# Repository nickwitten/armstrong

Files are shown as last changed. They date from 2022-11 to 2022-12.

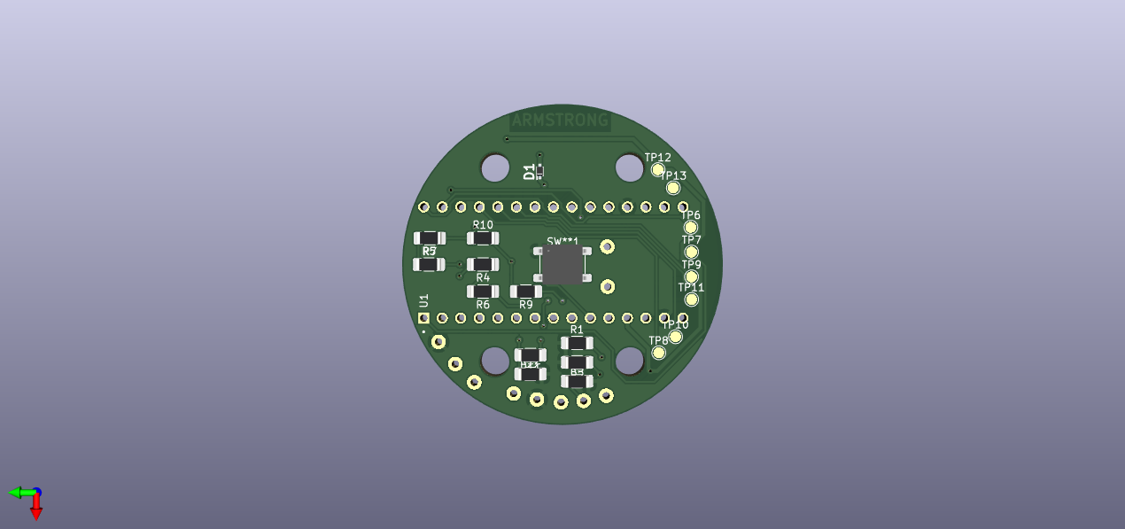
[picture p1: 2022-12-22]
poster_figures/Armstrong_v2.0_PCB_3D_Back.png

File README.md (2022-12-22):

# ARMSTRONG

Armstrong is a functional electrical stimulation (FES) project aimed to help individuals with spinal chord injuries. The loss of dexterity in the fingers and hand makes day-to-day life much more difficult. The wearable watch has two electrodes that are placed on the user's arm to stimulate the forearm muscles which elicits a grasping motion.

The project contains two PCB designs located in
/ArmstrongPCB/
for a transformer based stimulation circuit and also a boost/H-bridge based stimulation circuit for more waveform options and amplitude.

The project also contains the firmware located in
/ArmstrongSoftware/
which can be flashed to an Arduino. There is separate firmware for the transformer based circuit and the boost/H-bridge based circuit.

The directory
/deliverables/
contains all of the design files that were used in the final product. A lot of other folders were used for exploring ideas and debugging.

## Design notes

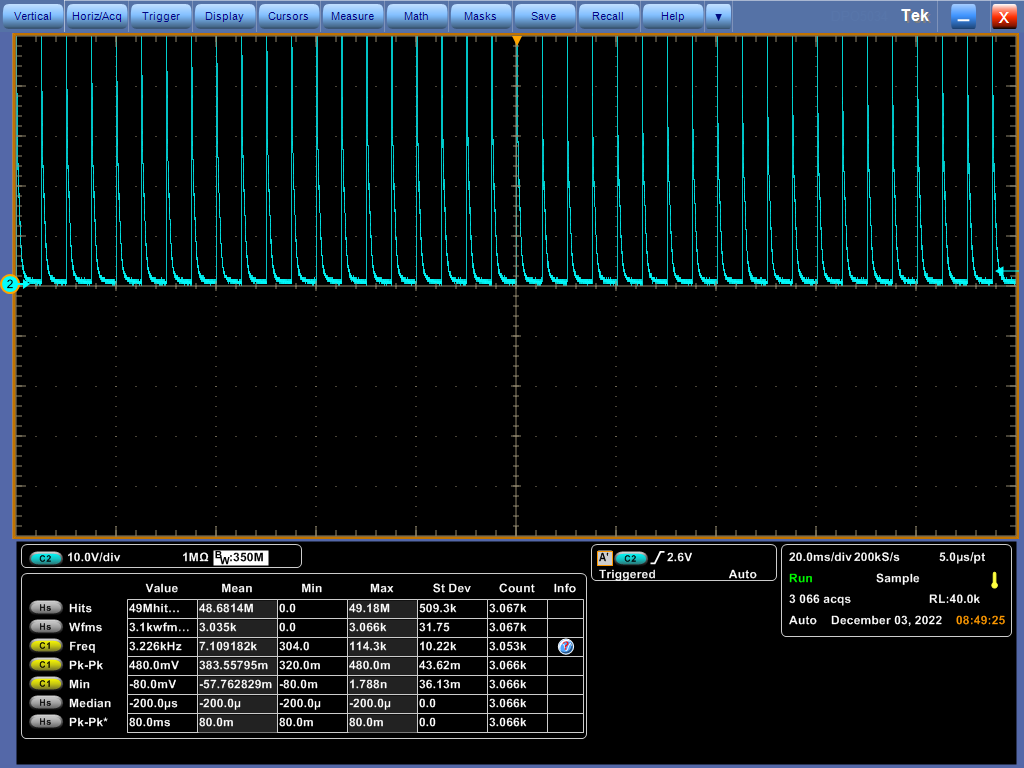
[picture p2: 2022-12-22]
poster_figures/wave_pulse.png

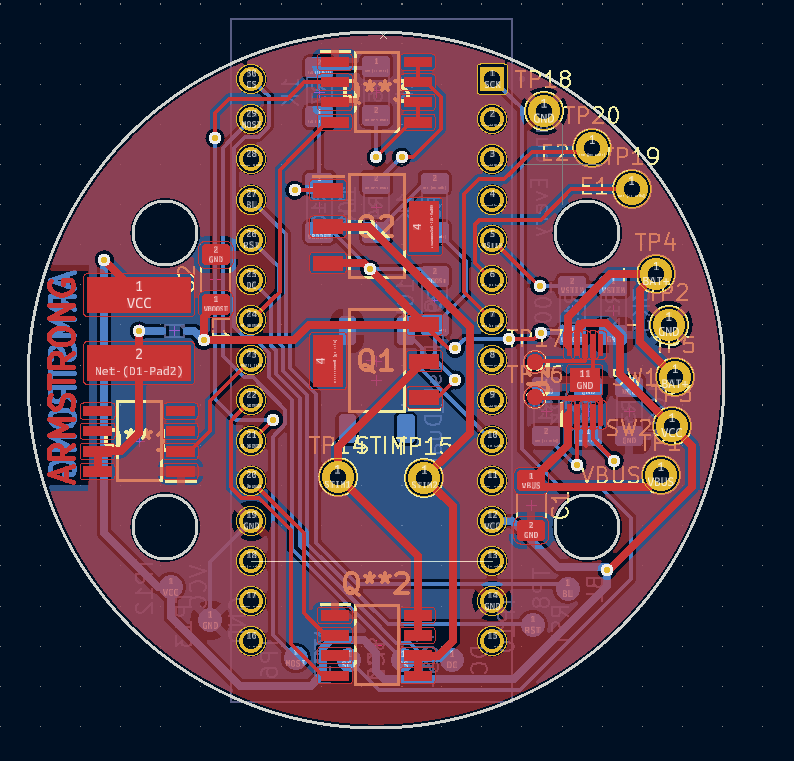
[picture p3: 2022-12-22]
poster_figures/Armstrong_v2.0_PCB_Layout..png

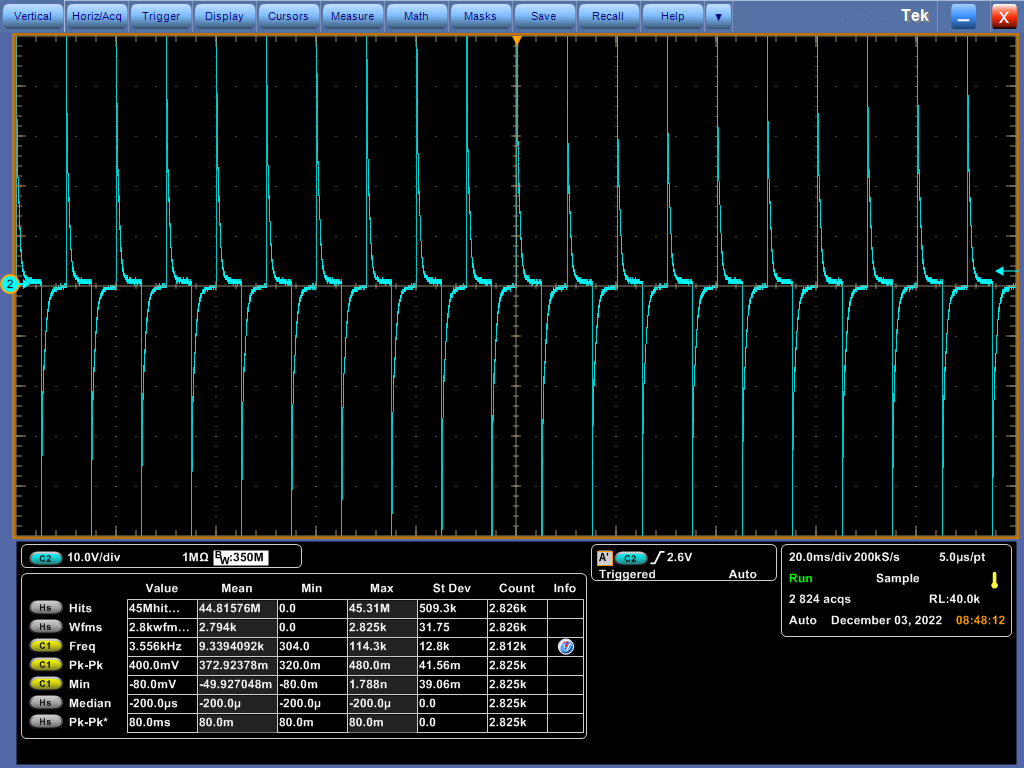
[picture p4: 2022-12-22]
poster_figures/wave_differential_high_amp.png

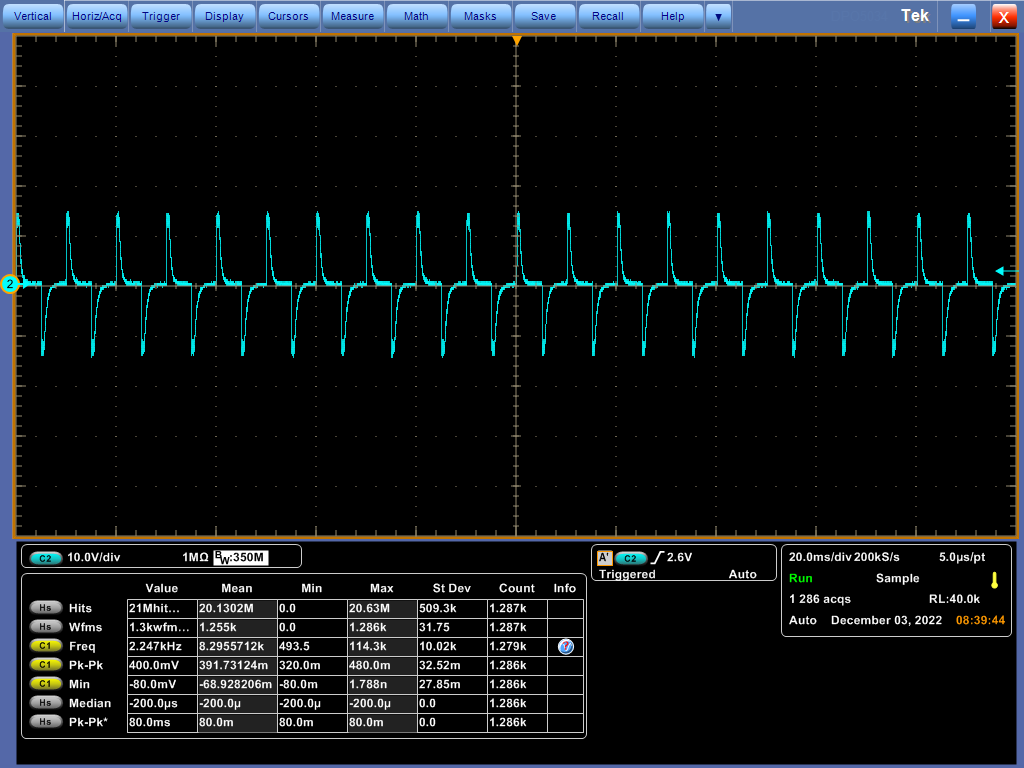
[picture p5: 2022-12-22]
poster_figures/wave_differential_low_amp.png

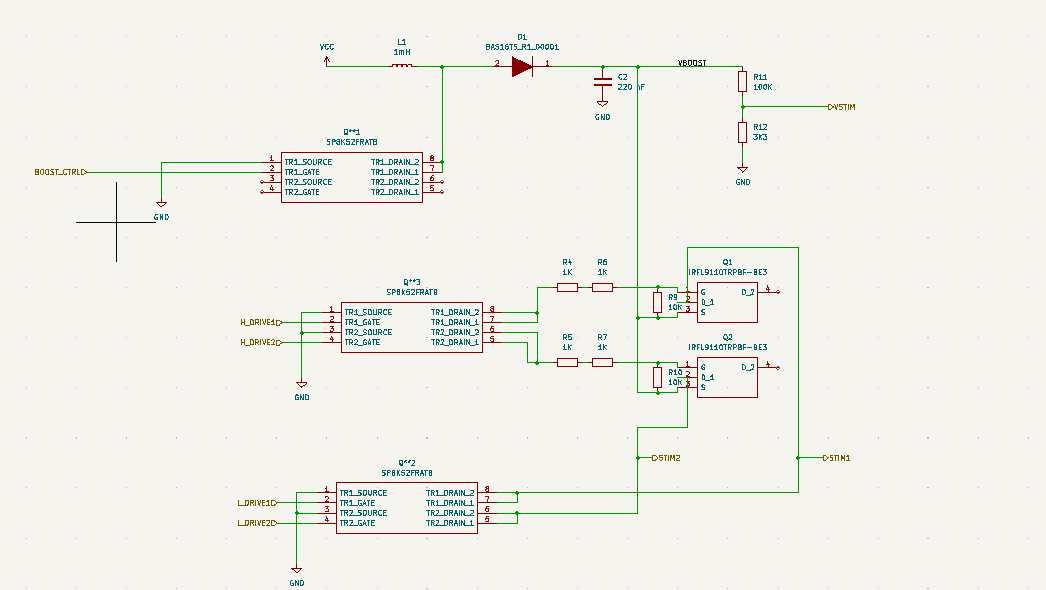
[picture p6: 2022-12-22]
poster_figures/Armstrong_v2.0_Schematic_Stim.png

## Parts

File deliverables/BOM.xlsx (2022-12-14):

 | Item | Supplier | Part# | Manufacturer# | Description | Qty | Price
Primary | 1A | Amazon | GC9A01 | Waveshare | 1.28 Inch Round LCD | 2 | $41.38
Direct Link: | https://www.amazon.com/1-28inch-Display-Resolution-Interface-Raspberry/dp/B08VGT2T42/
Alternative | 1B | Waveshare | GC9A01 | Waveshare | 1.28 Inch Round LCD | 2 | $41.38
Direct Link: | https://www.waveshare.com/product/1.28inch-lcd-module.htm
Primary | 2A | Amazon | B072CFZX8W | JAYSSS | 0.2mm Copper Sheet | 2 | $27.80
Direct Link: | https://www.amazon.com/0-2mm-Thickness-Copper-Purity-100mmx1000mm/dp/B07ZCFZX8W/
Alternative | 2B | Amazon | B098YZ16Y9 | Craft Wire | 32 Guage Copper Sheet | 2 | $37.98
Direct Link: | https://www.amazon.com/99-9-Copper-Sheet-Gauge-Blank/dp/B098YZ16Y9?th=1
Primary | 3A | Digikey | 2449-CS1204AF260CT-ND - Cut Tape (CT) | CIT Relay and Switch | SMD Tactile Button | 10 | $3.81
Direct Link: | https://www.digikey.com/en/products/detail/cit-relay-and-switch/CS1204AF260/12502958
Alternative | 3B | If Can't Buy Let Us Know
Direct Link:
 | Item | Supplier | Part# | Manufacturer# | Description | Qty | Price
Primary | 4A | Amazon | a19101700ux0341 | uxcell | uxcell 6710-2RS Deep Groove Ball Bearings 50mm x 62mm x 6mm Double Sealed Chrome Steel Z2 ABEC1 | 2 | $19.98
Direct Link: | https://www.amazon.com/uxcell-6710-2RS-Groove-Bearings-Double/dp/B085NDHJ8F?th=1
Alternative | 4B | AliExpress | 6710ZZ | Sunshine Xixi | 1pcs ultra-thin deep groove ball bearings 6710ZZ 50*62*6 mm | 2 | $13.86
Direct Link: | https://www.aliexpress.us/item/2251832472419159.html
Primary | 5A | Digikey | MT4148-ND | MET-23 | TRANSFORMER 1.6KCT:3.2 2.5MADC | 2 | $23.20
Direct Link: | https://www.digikey.com/en/products/detail/tamura/MET-23/285665
Alternative | 5B
Direct Link:
 | Item | Supplier | Part# | Manufacturer# | Description | Qty | Price
Primary | 6A | Texas Instruments | LM2937ES-3.3-ND | LM2937ES-3.3 | IC REG LIN 3.3V 500MA DDPAK | 5 | $16.70
Direct Link: | https://www.digikey.com/en/products/detail/texas-instruments/LM2937ES-3-3/3701317
Alternative | 6B
Direct Link:
Primary | 7A |  |  |  | Battery Packs 3.7 V 250mAh 31.5 x 17.0 x 5.7mm
Direct Link: | https://www.mouser.com/ProductDetail/Renata/ICP521630PM?qs=sGAEpiMZZMuXcNZ31nzYhXht66AyoktbAomnvfkiFzU%3D
Alternative | 7B
Direct Link:
 | Item | Supplier | Part# | Manufacturer# | Description | Qty | Price
Primary | 8A | ROHM Semiconductor | 755-SP8K52FRATB | SP8K52FRATB | MOSFET Nch+Nch 100V Vds 3A 0.135Rds(on) 8.5Qg | 5 | $5.55
Direct Link: | https://www.mouser.com/ProductDetail/ROHM-Semiconductor/SP8K52FRATB?qs=sGAEpiMZZMutXGli8Ay4kEWj9pzNwJQ3Ab9nciqoLcQ%3D
Alternative | 8B | ROHM Semiconductor | 755-UM6K31NFHATCN | UM6K31NFHATCN | MOSFET Nch+Nch 60V Vds 3Rds(on) SOT-363 | 5 | $2.60
Direct Link: | https://www.mouser.com/ProductDetail/ROHM-Semiconductor/UM6K31NFHATCN?qs=sGAEpiMZZMutXGli8Ay4kEWj9pzNwJQ3hyJfQAX8x7s%3D
Primary | 9A | Panjit | 241-BAS16TS_R1_00001 | BAS16TS_R1_00001 | Diodes - General Purpose, Power, Switching 100Vll Signal Switching Diodes 4A | 10 | $1.56
Direct Link: | https://www.mouser.com/ProductDetail/Panjit/BAS16TS_R1_00001?qs=sPbYRqrBIVkk0IRTyt6GmQ%3D%3D
Alternative | 9B | onsemi / Fairchild | 512-MMSD4448 | MMSD4448 | Diodes - General Purpose, Power, Switching Hi Conductance Fast | 10 | $2.51
Direct Link: | https://www.mouser.com/ProductDetail/onsemi-Fairchild/MMSD4448?qs=HxNY1oXTrTS1XYzDYVbdxA%3D%3D
Primary | 10A | Analog Devices | 584-ADP122AUJZ-3.3R7 | ADP122AUJZ-3.3-R7 | Linear Voltage Regulators 300mA LDO 3.3Vout | 5 | $8.20
Direct Link: | https://www.mouser.com/ProductDetail/Analog-Devices/ADP122AUJZ-3.3-R7?qs=BpaRKvA4VqERsawSFjb%252Blw%3D%3D
Alternative | 10B | Analog Devices | 584-ADP160AUJZ-3.3R7 | ADP160AUJZ-3.3-R7 | Linear Voltage Regulators 150mA LDO 3.3Vout w/ QOD | 5 | $8.00
Direct Link: | https://www.mouser.com/ProductDetail/Analog-Devices/ADP160AUJZ-3.3-R7?qs=WIvQP4zGanjwQREaBvEWig%3D%3D
Primary | 11A | Analog Devices | 584-ADP162AUJZ-4.2R7 | ADP162AUJZ-4.2-R7 | LDO Voltage Regulators 150mA LDO 4.2Vout | 5 | $8.00
Direct Link: | https://www.mouser.com/ProductDetail/Analog-Devices/ADP162AUJZ-4.2-R7?qs=WIvQP4zGangti17mGJlz9g%3D%3D
Alternative | 11B | Texas Instruments | 595-TPS79942DDCR | TPS79942DDCR | LDO Voltage Regulators Sgl Output LDO 200mA Fixed 4.2V | 5 | $5.20
Direct Link: | https://www.ti.com/lit/ds/symlink/tps799.pdf?HQS=dis-mous-null-mousermode-dsf-pf-null-wwe&ts=1665556814501
 | Item | Supplier | Part# | Manufacturer# | Description | Qty | Price
Primary | 12A | Mouser | 782-ABX00033 | ABX00033 | AVR ARDUINO NANO EVERY | 2 | $33.76
Direct Link: | https://www.mouser.com/ProductDetail/Arduino/ABX00033?qs=PzGy0jfpSMueXyfBfl2XSA%3D%3D
Alternative | 12B | Digikey | 1050-ABX00033-ND | ABX00033 | ARDUINO NANO EVERY WITH HEADERS | 2 | $33.76
Direct Link: | https://www.digikey.com/en/products/detail/arduino/ABX00033/10239972
 | Item | Supplier | Part# | Manufacturer# | Description | Qty | Price
Primary | 13A | Mouser | 755-SP8K52FRATB | SP8K52FRATB | MOSFET Nch+Nch 100V Vds 3A 0.135Rds(on) 8.5Qg | 5 | $5.55
Direct Link: | https://www.mouser.com/ProductDetail/ROHM-Semiconductor/SP8K52FRATB?qs=sGAEpiMZZMutXGli8Ay4kEWj9pzNwJQ3Ab9nciqoLcQ%3D
Alternative | 13B
Direct Link:
Primary | 14A | Mouser | 241-BAS16TS_R1_00001 | BAS16TS_R1_00001 | Diodes - General Purpose, Power, Switching 100Vll Signal Switching Diodes 4A | 10 | $1.56
Direct Link: | https://www.mouser.com/ProductDetail/Panjit/BAS16TS_R1_00001?qs=sPbYRqrBIVkk0IRTyt6GmQ%3D%3D
Alternative | 14B
Direct Link:
Primary | 15A | Mouser | 78-IRFL9110TRPBF-BE3 | IRFL9110TRPBF-BE3 | MOSFET 100V P-CH MOSFET (D-S) | 5 | $10.50
Direct Link: | https://www.mouser.com/ProductDetail/Vishay-Siliconix/IRFL9110TRPBF-BE3?qs=7MVldsJ5UaxpERaG2Aoxtg%3D%3D
Alternative | 15B
Direct Link:
Primary | 16A | Mouser | 595-BQ24093DGQR | BQ24093DGQR | Battery Management 1A,Sgl-Inp,Sgl-Cell Li-Ion Batt Charger | 5 | $8.45
Direct Link: | https://www.mouser.com/ProductDetail/Texas-Instruments/BQ24093DGQR?qs=C44r%252BX3hXgJJomV3RK43zw%3D%3D
Alternative | 16B
Direct Link:
Primary | 17A | Mouser | 994-LPS6225-105MRC | LPS6225-105MRC | Power Inductors - SMD 1 mH Shld 20% 170mA 6Ohms | 5 | $9.10
Direct Link: | https://www.mouser.com/ProductDetail/Coilcraft/LPS6225-105MRC?qs=QQJxVsr8EGZFFDxesxNmXA%3D%3D
Alternative | 17B
Direct Link:
Primary | 18A | Mouser | 80-C1206C105K3NAUTO | C1206C105K3NACAUTO | SMD/SMT 25V 1uF X8L 1206 | 10 | $5.30
Direct Link: | https://www.mouser.com/ProductDetail/KEMET/C1206C105K3NACAUTO
Alternative | 18B | Mouser | 80-C1206F105M5RAUTLR | C1206F105M5RACAUTO7210 | SMD/SMT 50V 1uF X7R 1206 | 10 | $7.30
Direct Link: | https://www.mouser.com/ProductDetail/KEMET/C1206F105M5RACAUTO7210
Primary | 19A | Mouser | 80-C1206C224J1RAUTO | C1206C224J1RACAUTO | SMD/SMT 100V 0.22uF X7R 1206 5% AEC-Q200 | 10 | $8.30
Direct Link: | https://www.mouser.com/ProductDetail/KEMET/C1206C224J1RACAUTO?qs=ds50AKTGxA8%252BykFr3yWSoQ%3D%3D
Alternative | 19B | Mouser | 81-GCJ31MR72A224KA1L | GCJ31MR72A224KA01L | SMD/SMT .22UF 100V 10% 1206 | 10 | $4.80
Direct Link: | https://www.mouser.com/ProductDetail/Murata-Electronics/GCJ31MR72A224KA01L?qs=zThidflJDvanaGTB%252BAWhhA%3D%3D
Primary | 20A | Mouser | 71-RCC12061K00FKEA | RCC12061K00FKEA | SMD 1.0 Kohms 1% 100ppm | 20 | $6.60
Direct Link: | https://www.mouser.com/ProductDetail/Vishay-Dale/RCC12061K00FKEA
Alternative | 20B | Mouser | 755-SFR18EZPF1001 | SFR18EZPF1001 | Thick Film Resistors - SMD | 20 | $9.60
Direct Link: | https://www.mouser.com/ProductDetail/ROHM-Semiconductor/SFR18EZPF1001
Primary | 21A | Mouser | 71-CRMA1206AF10K0DKF | CRMA1206AF10K0DKEF | Thick Film Resistors - SMD 0.30W 10Kohm .5% AEC-Q200 | 10 | $5.90
Direct Link: | https://www.mouser.com/ProductDetail/Vishay/CRMA1206AF10K0DKEF?qs=sGAEpiMZZMtlubZbdhIBIOn2mbhvx7T2u0J1JQj7TEY%3D
Alternative | 21B
Direct Link:
Primary | 22A | Mouser | 71-CRMA1206AF100KFKF | CRMA1206AF100KFKEF | Thick Film Resistors - SMD 0.30W 100Kohm 1% AEC-Q200 | 10 | $5.50
Direct Link: | https://www.mouser.com/ProductDetail/Vishay/CRMA1206AF100KFKEF?qs=QNEnbhJQKvZE9rjcxNiRnA%3D%3D
Alternative | 22B
Direct Link:
Primary | 23A | Mouser | 755-SFR18EZPJ332 | SFR18EZPJ332 | Thick Film Resistors - SMD | 10 | $1.39
Direct Link: | https://www.mouser.com/ProductDetail/ROHM-Semiconductor/SFR18EZPJ332?qs=sGAEpiMZZMtlubZbdhIBIK8AeiPKd8jIg8Se9AlDaOM%3D
Alternative | 23B
Direct Link:
Primary | 24A | Mouser | 755-SFR18EZPF2001 | SFR18EZPF2001 | Thick Film Resistors - SMD | 10 | $2.15
Direct Link: | https://www.mouser.com/ProductDetail/ROHM-Semiconductor/SFR18EZPF2001?qs=sGAEpiMZZMtlubZbdhIBIK8AeiPKd8jIOdUsMKoQsaE%3D
Alternative | 24B
Direct Link:
Primary | 25A | Mouser | 71-TNPW12062K70BEEA | TNPW12062K70BEEA | Thick Film Resistors - SMD | 10 | $7.59
Direct Link: | https://www.mouser.com/ProductDetail/Vishay-Dale/TNPW12062K70BEEA?qs=sGAEpiMZZMtlubZbdhIBIKjNc5kvbugN9Cb1dArGElQ%3D
Alternative | 25B
Direct Link:

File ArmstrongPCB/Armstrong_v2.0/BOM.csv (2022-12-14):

Id | Designator | Package | Quantity | Designation | Supplier and ref
1 | SW**1 | CS1204AF260-SMD | 1 | SW_Push_Dual
2 | TP17 | TestPoint_Pad_D1.0mm | 1 | ~{CHG}
3 | TP16 | TestPoint_Pad_D1.0mm | 1 | PG
4 | C2 | C_1206_3216Metric_Pad1.33x1.80mm_HandSolder | 1 | 220 nF
5 | C1 | C_1206_3216Metric_Pad1.33x1.80mm_HandSolder | 1 | 1uF
6 | D1 | BAS16TS_R1_00001 | 1 | BAS16TS_R1_00001
7 | R12 | R_1206_3216Metric_Pad1.30x1.75mm_HandSolder | 1 | 3K3
8 | R11,R3 | R_1206_3216Metric_Pad1.30x1.75mm_HandSolder | 2 | 100K
9 | R10,R9 | R_1206_3216Metric_Pad1.30x1.75mm_HandSolder | 2 | 10K
10 | R7,R6,R5,R4 | R_1206_3216Metric_Pad1.30x1.75mm_HandSolder | 4 | 1K
11 | R2 | R_1206_3216Metric_Pad1.30x1.75mm_HandSolder | 1 | 2K
12 | R1 | R_1206_3216Metric_Pad1.30x1.75mm_HandSolder | 1 | 2K7
13 | TP13 | TestPoint_Pad_D1.5mm | 1 | GND
14 | TP12 | TestPoint_Pad_D1.5mm | 1 | VCC
15 | TP11 | TestPoint_Pad_D1.5mm | 1 | DC
16 | TP10 | TestPoint_Pad_D1.5mm | 1 | RST
17 | TP9 | TestPoint_Pad_D1.5mm | 1 | CS
18 | TP8 | TestPoint_Pad_D1.5mm | 1 | BL
19 | TP7 | TestPoint_Pad_D1.5mm | 1 | SCK
20 | TP6 | TestPoint_Pad_D1.5mm | 1 | MOSI
21 | TP4 | TestPoint_THTPad_D2.0mm_Drill1.0mm | 1 | BAT+
22 | TP3 | TestPoint_THTPad_D2.0mm_Drill1.0mm | 1 | SW2
23 | Q**2,Q**3,Q**1 | SP8K52FRATB | 3 | SP8K52FRATB
24 | TP15 | TestPoint_THTPad_D2.0mm_Drill1.0mm | 1 | STIM2
25 | U1 | Nano Every | 1 | Nano Every
26 | L1 | LPS6225-105MRC | 1 | 1mH
27 | TP14 | TestPoint_THTPad_D2.0mm_Drill1.0mm | 1 | STIM1
28 | TP2 | TestPoint_THTPad_D2.0mm_Drill1.0mm | 1 | BAT-
29 | TP5 | TestPoint_THTPad_D2.0mm_Drill1.0mm | 1 | SW1
30 | Q2,Q1 | IRFL9110TRPBF-BE3 | 2 | IRFL9110TRPBF-BE3
31 | U2 | BQ24093DGQR | 1 | BQ24093DGQR
32 | TP1 | TestPoint_THTPad_D2.0mm_Drill1.0mm | 1 | VBUS

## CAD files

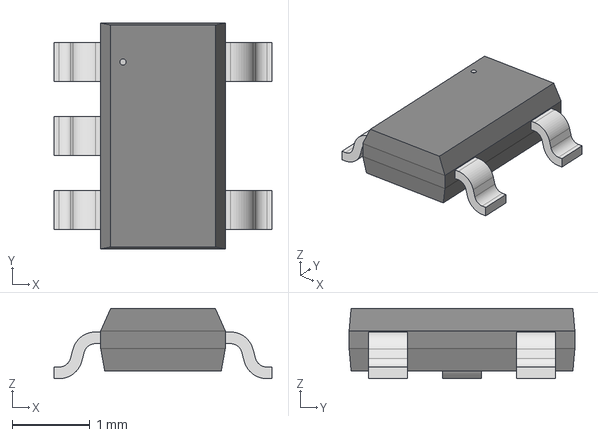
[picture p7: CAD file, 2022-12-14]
ArmstrongPCB/Armstrong_circuit/3D/ADP122AUJZ-3-3-R7.stp
2.80 x 2.90 x 0.903 mm

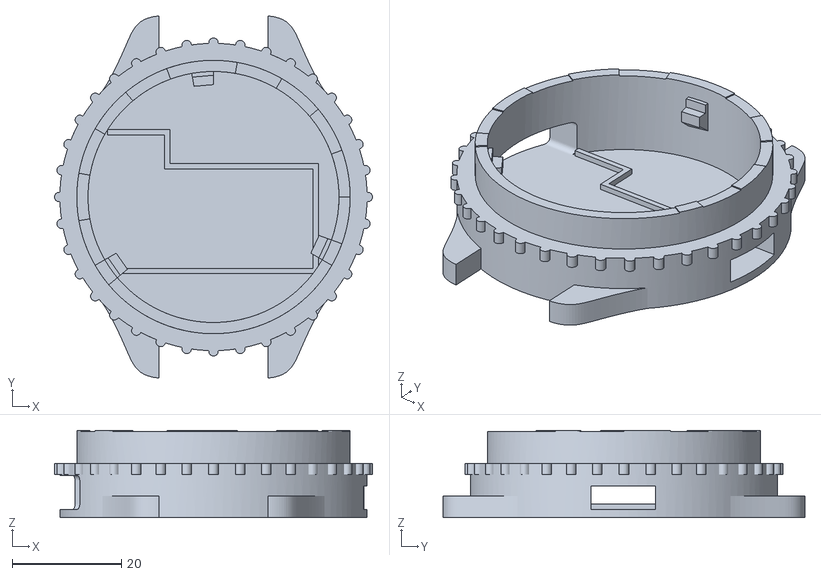
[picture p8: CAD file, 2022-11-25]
deliverables/mechanical/Base.stl
58.2 x 66.2 x 16.0

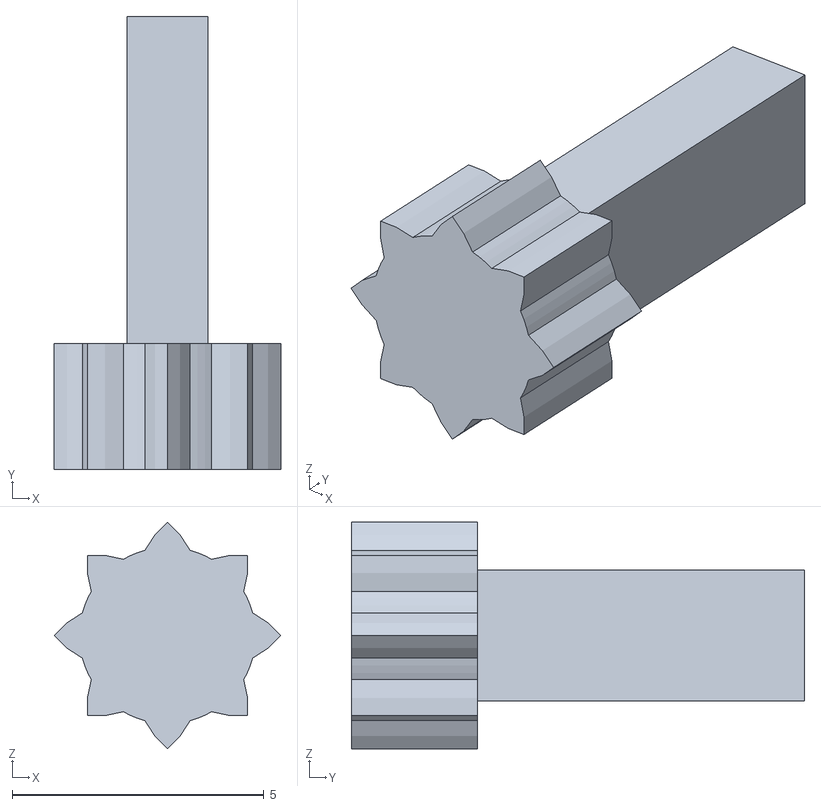
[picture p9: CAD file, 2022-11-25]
print_1/Shaft.stl
4.50 x 9.00 x 4.50

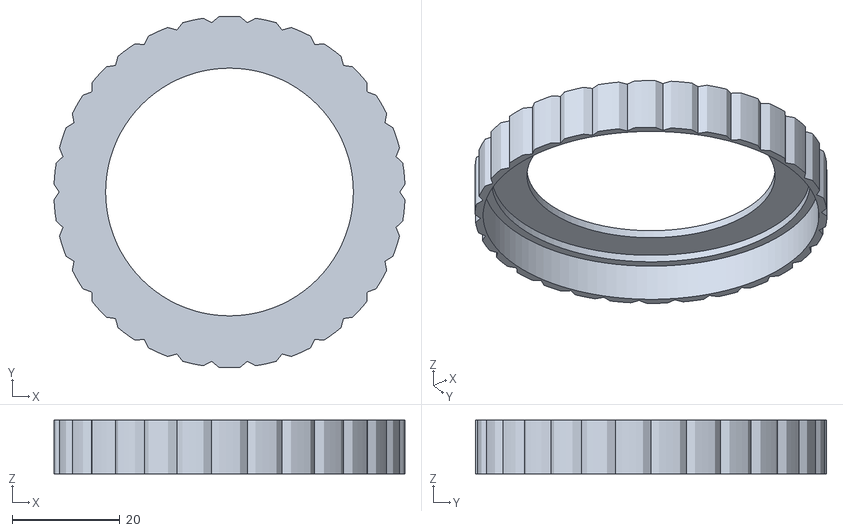
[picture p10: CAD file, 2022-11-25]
print_2/Bezel.stl
65.1 x 65.2 x 10.0

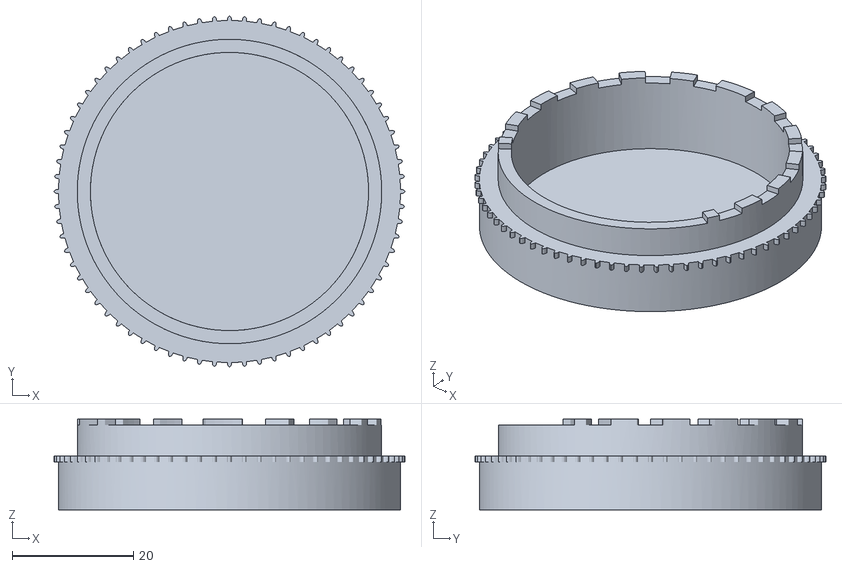
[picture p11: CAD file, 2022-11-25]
print_3/Base.stl
58.0 x 58.0 x 15.0

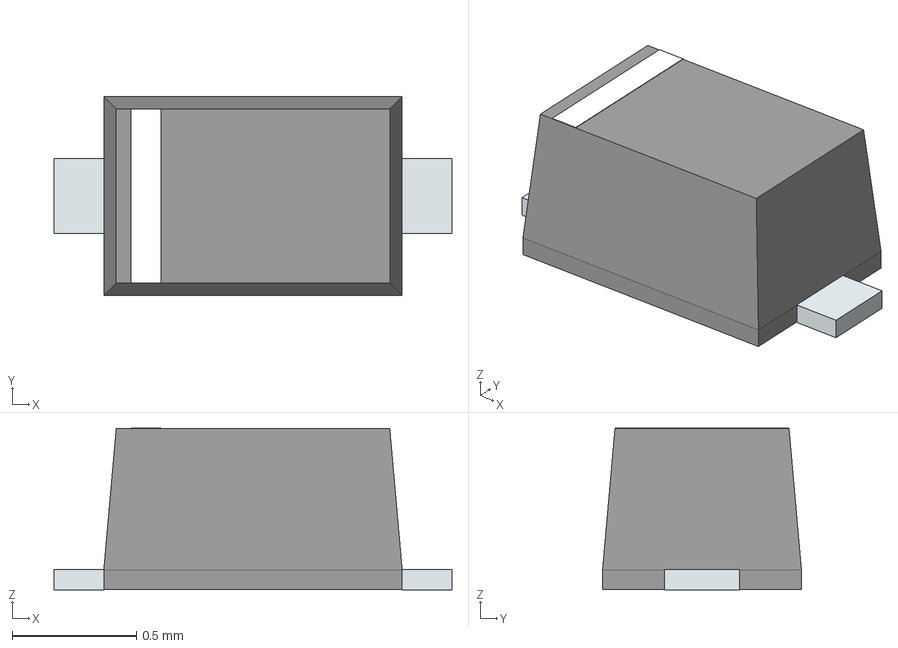
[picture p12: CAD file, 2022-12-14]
ArmstrongPCB/Armstrong_circuit/3D/BAS16TS_R1_00001.stp
1.60 x 0.8 x 0.65 mm
PinKIdent
PinK
PinA

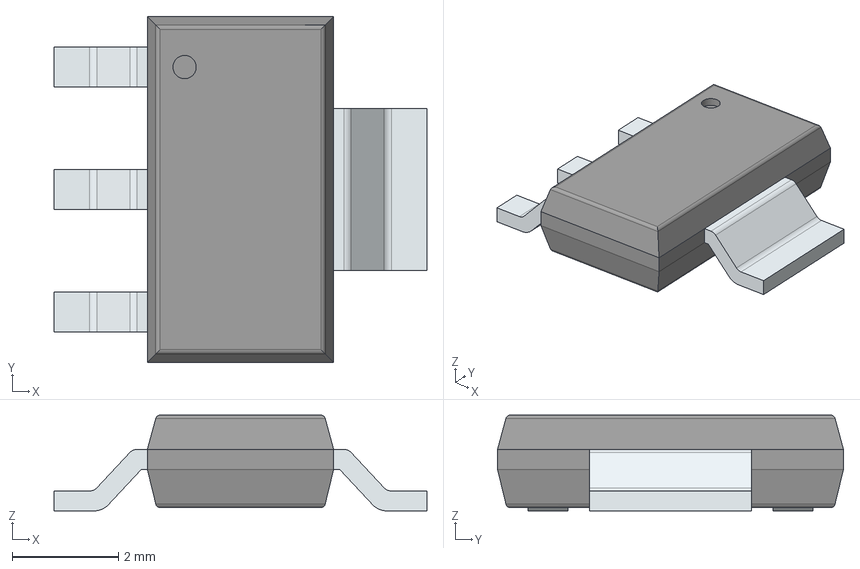
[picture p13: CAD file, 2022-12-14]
ArmstrongPCB/Armstrong_v2.0/3D/IRFL9110TRPBF-BE3.stp
7.00 x 6.50 x 1.80 mm
PinsArrayL
FilletPinR

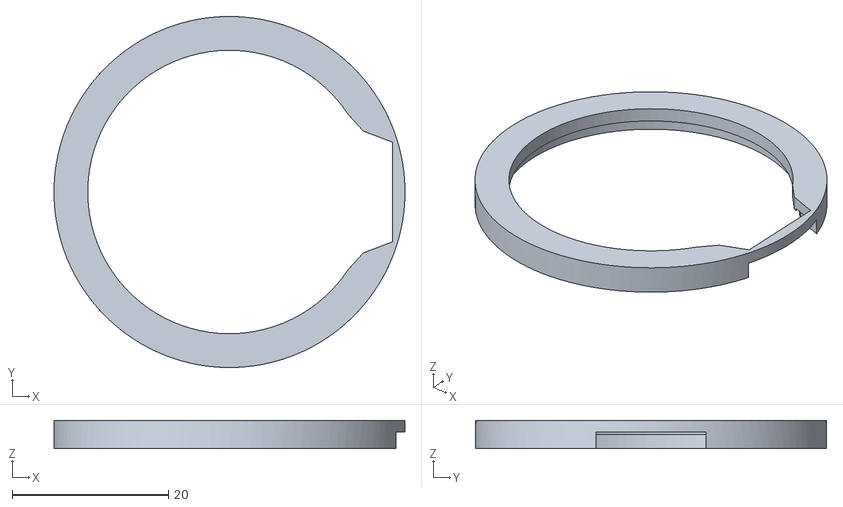
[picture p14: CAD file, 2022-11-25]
deliverables/mechanical/Screen.stl
45.0 x 45.0 x 3.60

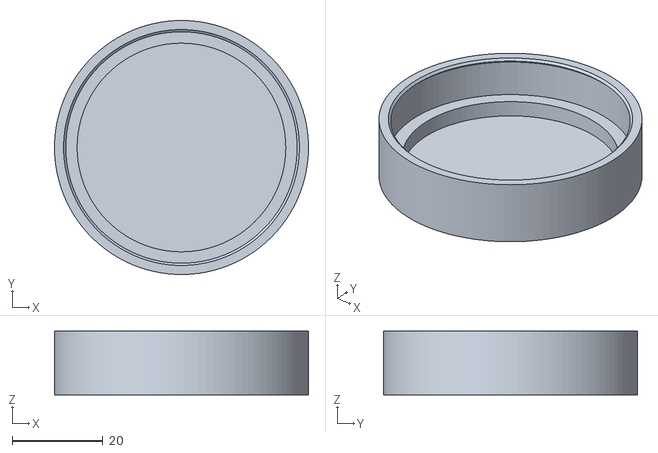
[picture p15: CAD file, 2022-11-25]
print_1/Base.stl
56.0 x 56.0 x 14.0

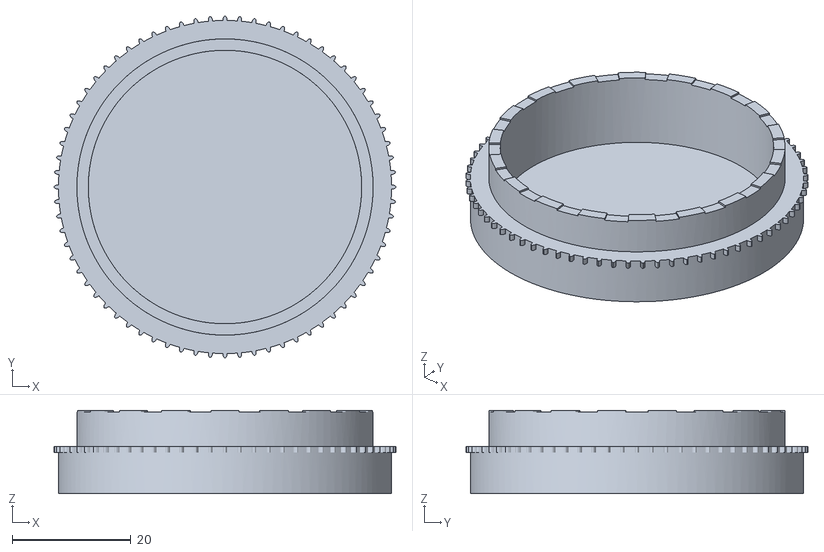
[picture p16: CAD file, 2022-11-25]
print_2/Base.stl
57.5 x 57.5 x 14.0

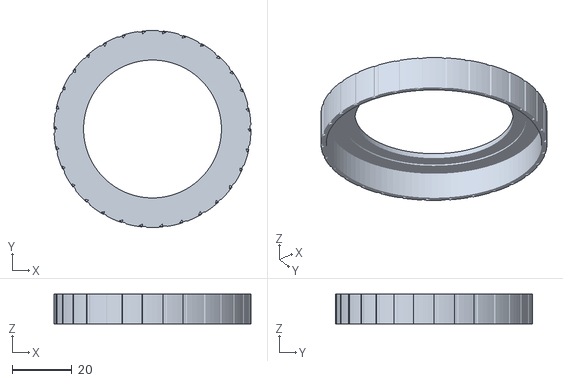
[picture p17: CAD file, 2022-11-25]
print_3/Bezel.stl
65.7 x 65.7 x 10.0

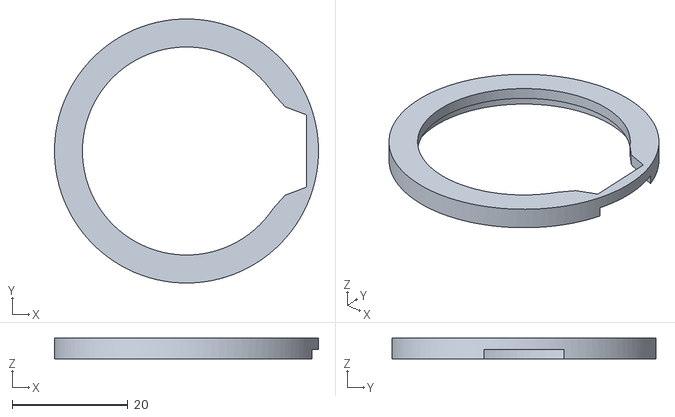
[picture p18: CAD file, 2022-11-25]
print_4/WATCH_SCREEN_SUPPORT.stl
45.6 x 45.6 x 3.60

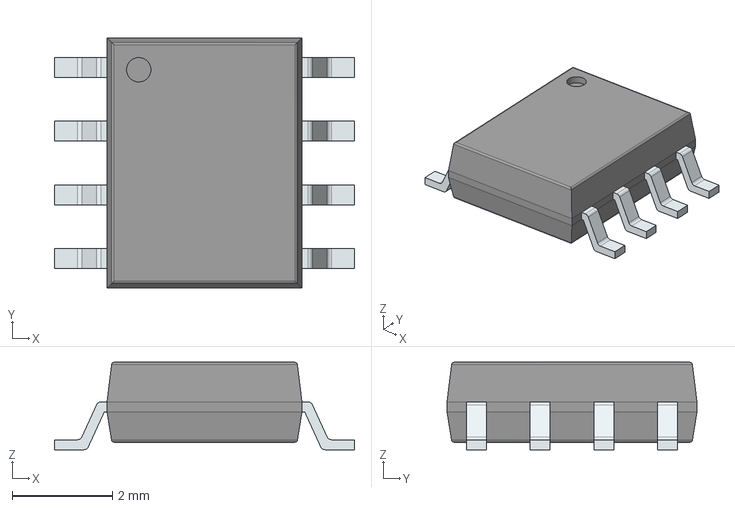
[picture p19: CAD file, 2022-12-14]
ArmstrongPCB/Armstrong_circuit/3D/SP8K52FRATB.stp
6.00 x 5.00 x 1.75 mm
PinsArrayLR

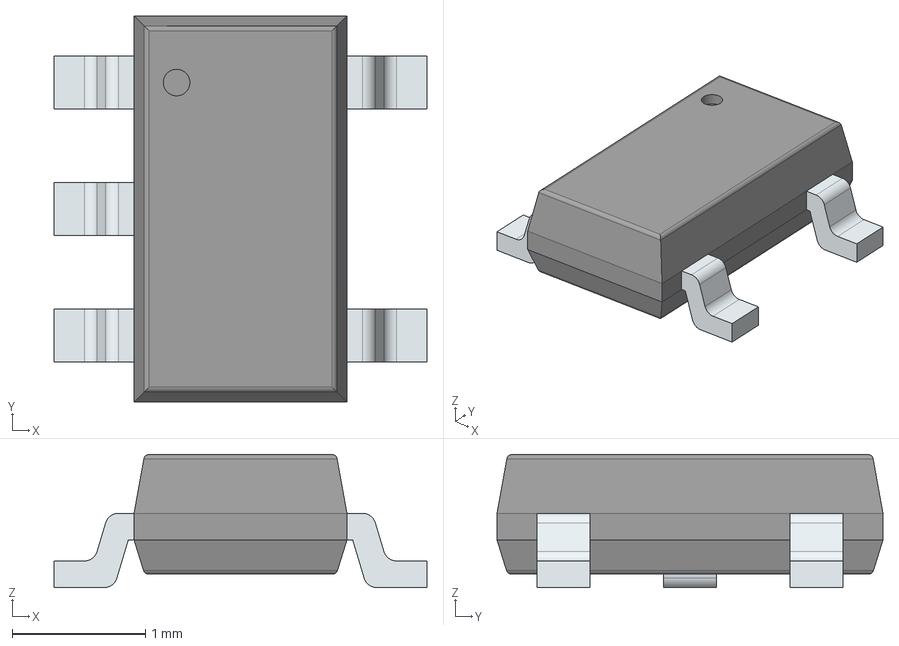
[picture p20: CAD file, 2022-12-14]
ArmstrongPCB/Armstrong_v2.0/3D/ADP162AUJZ-4.2-R7.stp
2.80 x 2.90 x 1.00 mm
PinsArrayL
PinsArrayR

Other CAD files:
print_4/WATCH_BASE.stl
deliverables/mechanical/Bezel.stl
print_1/Bezel.stl
ArmstrongPCB/Armstrong_circuit/3D/Armstrong_pcb_v1.stp
ArmstrongPCB/Armstrong_circuit/3D/MET-23.stp
ArmstrongPCB/Armstrong_circuit/3D/SON4_PTS526SM15SMTR2LFS_CNK.stp
ArmstrongPCB/Armstrong_v2.0/3D/Armstrong_pcb_v1.stp
ArmstrongPCB/Armstrong_v2.0/3D/BQ24093DGQR.stp
ArmstrongPCB/Armstrong_v2.0/3D/MET-23.stp
ArmstrongPCB/Armstrong_v2.0/3D/SON4_PTS526SM15SMTR2LFS_CNK.stp
deliverables/mechanical/Enclosure v49.f3z

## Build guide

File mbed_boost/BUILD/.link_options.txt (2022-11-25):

4DGL-uLCD-SE/uLCD_4DGL_Graphics.o 4DGL-uLCD-SE/uLCD_4DGL_Media.o 4DGL-uLCD-SE/uLCD_4DGL_Text.o 4DGL-uLCD-SE/uLCD_4DGL_main.o Motor/Motor.o RPCInterface/SerialRPCInterface.o RPCInterface/mbed-rpc/Arguments.o RPCInterface/mbed-rpc/RPCFunction.o RPCInterface/mbed-rpc/parse_pins.o RPCInterface/mbed-rpc/rpc.o SDFileSystem/FATFileSystem/ChaN/ccsbcs.o SDFileSystem/FATFileSystem/ChaN/diskio.o SDFileSystem/FATFileSystem/ChaN/ff.o SDFileSystem/FATFileSystem/FATDirHandle.o SDFileSystem/FATFileSystem/FATFileHandle.o SDFileSystem/FATFileSystem/FATFileSystem.o SDFileSystem/SDFileSystem.o main.o mbed-rtos/rtos/Mutex.o mbed-rtos/rtos/RtosTimer.o mbed-rtos/rtos/Semaphore.o mbed-rtos/rtos/Thread.o mbed-rtos/rtos/rtos_idle.o mbed-rtos/rtx/TARGET_CORTEX_M/HAL_CM.o mbed-rtos/rtx/TARGET_CORTEX_M/RTX_Conf_CM.o mbed-rtos/rtx/TARGET_CORTEX_M/TARGET_M3/TOOLCHAIN_GCC/HAL_CM3.o mbed-rtos/rtx/TARGET_CORTEX_M/TARGET_M3/TOOLCHAIN_GCC/SVC_Table.o mbed-rtos/rtx/TARGET_CORTEX_M/rt_CMSIS.o mbed-rtos/rtx/TARGET_CORTEX_M/rt_Event.o mbed-rtos/rtx/TARGET_CORTEX_M/rt_List.o mbed-rtos/rtx/TARGET_CORTEX_M/rt_Mailbox.o mbed-rtos/rtx/TARGET_CORTEX_M/rt_MemBox.o mbed-rtos/rtx/TARGET_CORTEX_M/rt_Memory.o mbed-rtos/rtx/TARGET_CORTEX_M/rt_Mutex.o mbed-rtos/rtx/TARGET_CORTEX_M/rt_OsEventObserver.o mbed-rtos/rtx/TARGET_CORTEX_M/rt_Robin.o mbed-rtos/rtx/TARGET_CORTEX_M/rt_Semaphore.o mbed-rtos/rtx/TARGET_CORTEX_M/rt_System.o mbed-rtos/rtx/TARGET_CORTEX_M/rt_Task.o mbed-rtos/rtx/TARGET_CORTEX_M/rt_Time.o mbed-rtos/rtx/TARGET_CORTEX_M/rt_Timer.o wave_player/wave_player.o X_NUCLEO_53L0A1/Components/VL53L0X/VL53L0X.o X_NUCLEO_53L0A1/XNucleo53L0A1.o ../mbed/TARGET_LPC1768/TOOLCHAIN_GCC_ARM/cmsis_nvic.o ../mbed/TARGET_LPC1768/TOOLCHAIN_GCC_ARM/mbed_board.o ../mbed/TARGET_LPC1768/TOOLCHAIN_GCC_ARM/retarget.o ../mbed/TARGET_LPC1768/TOOLCHAIN_GCC_ARM/startup_LPC17xx.o ../mbed/TARGET_LPC1768/TOOLCHAIN_GCC_ARM/system_LPC17xx.o

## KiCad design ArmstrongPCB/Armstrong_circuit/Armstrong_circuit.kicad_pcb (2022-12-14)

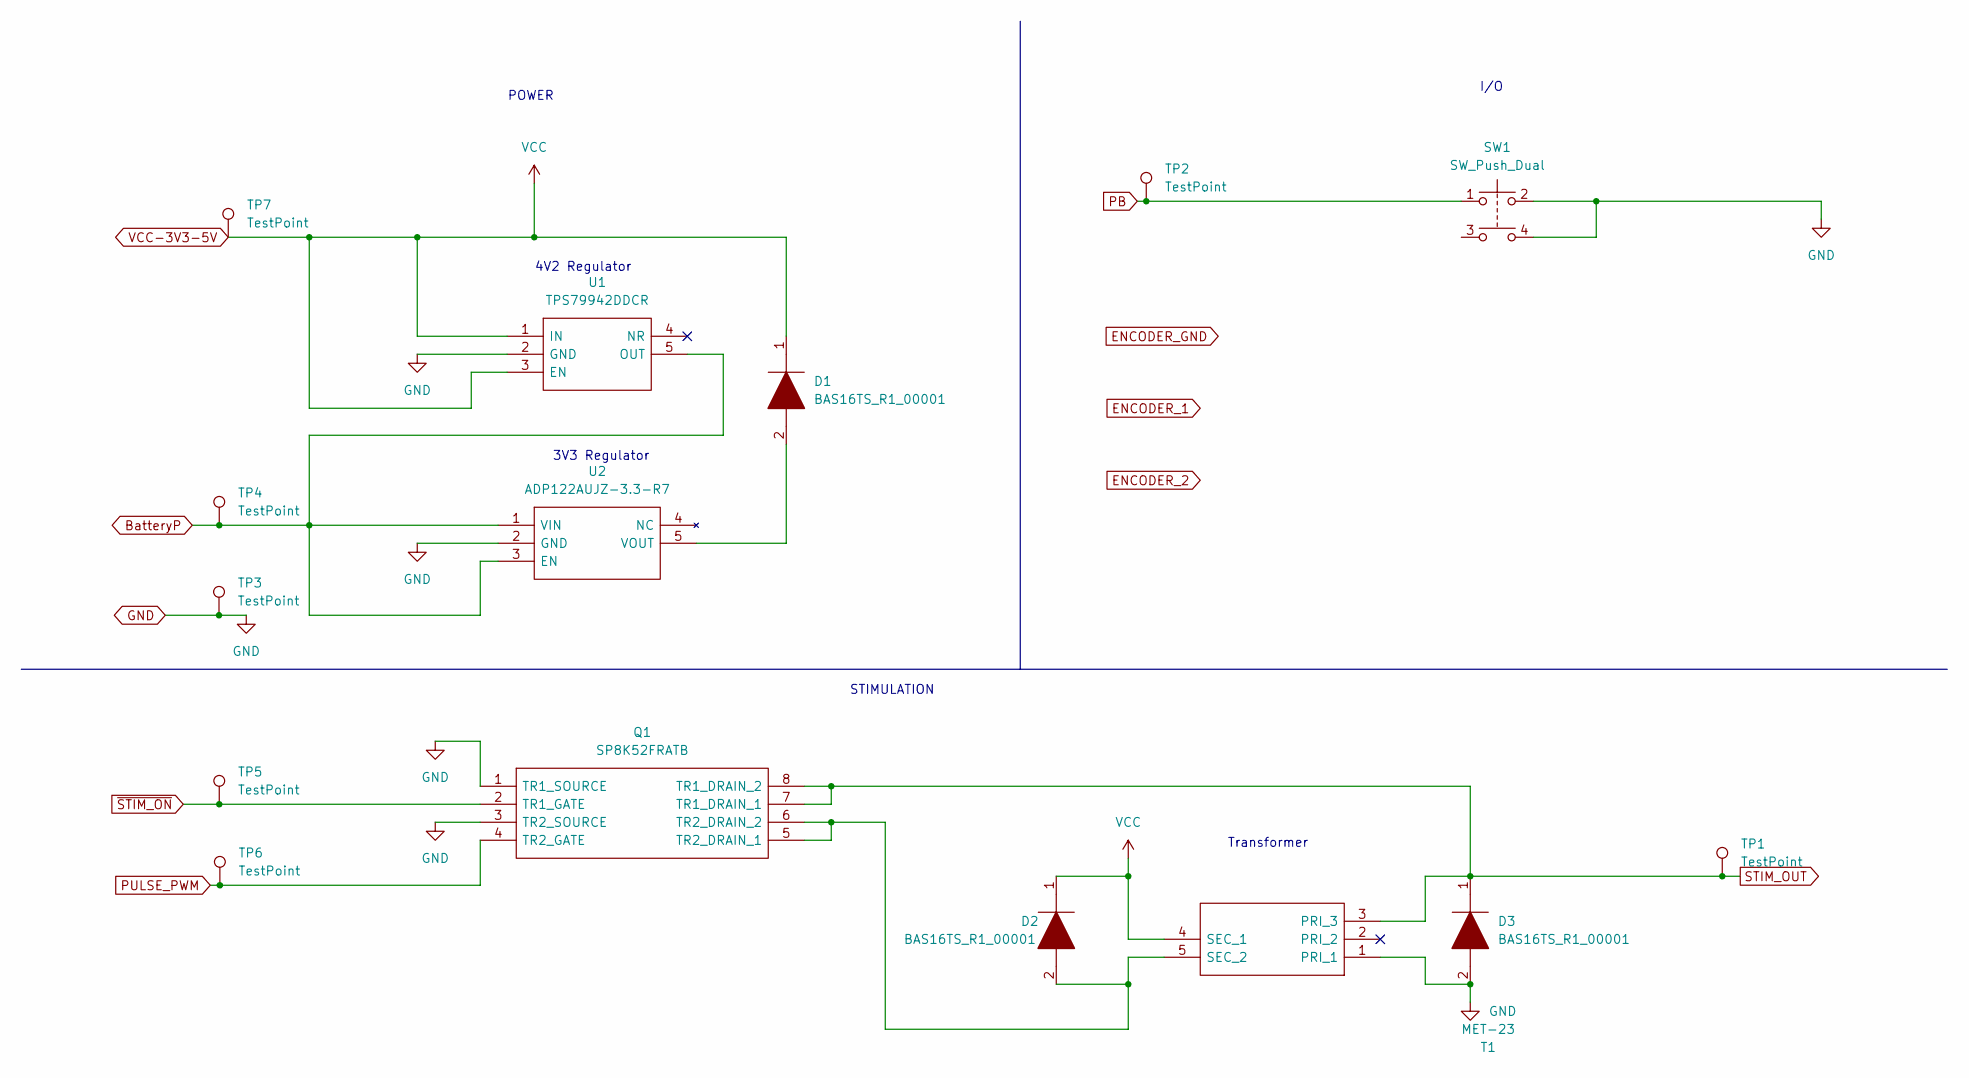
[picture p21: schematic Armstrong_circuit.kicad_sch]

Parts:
D1, D2, D3: BAS16TS_R1_00001; Manufacturer_Part_Number BAS16TS_R1_00001; Mouser Part Number 241-BAS16TS_R1_00001
Q1: SP8K52FRATB; Manufacturer_Part_Number SP8K52FRATB; Mouser Part Number 755-SP8K52FRATB
SW1: SW_Push_Dual; CS1204AF260-SMD
T1: MET-23; MET-23-SIDE; Manufacturer_Part_Number MET-23; Mouser Part Number 838-MET-23
TP1, TP2, TP3, TP4, TP5, TP6, TP7: TestPoint; TestPoint_Pad_1.0x1.0mm
U1: TPS79942DDCR; ADP162AUJZ-4.2-R7; Manufacturer_Part_Number TPS79942DDCR; Mouser Part Number 595-TPS79942DDCR
U2: ADP122AUJZ-3.3-R7; Manufacturer_Part_Number ADP122AUJZ-3.3-R7; Mouser Part Number 584-ADP122AUJZ-3.3R7

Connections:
BatteryP: TP4.1, U1.5 (OUT), U2.1 (VIN), U2.3 (EN)
GND: D3.2, Q1.1 (TR1_SOURCE), Q1.3 (TR2_SOURCE), SW1.2, SW1.4, T1.1 (PRI_1), TP3.1, U1.2 (GND), U2.2 (GND)
unnamed: D1.2, U2.5 (VOUT)
unnamed: D2.2, Q1.5 (TR2_DRAIN_1), Q1.6 (TR2_DRAIN_2), T1.5 (SEC_2)
PB: SW1.1, TP2.1
PULSE_PWM: Q1.4 (TR2_GATE), TP6.1
STIM_OUT: D3.1, Q1.7 (TR1_DRAIN_1), Q1.8 (TR1_DRAIN_2), T1.3 (PRI_3), TP1.1
VCC-3V3-5V: D1.1, D2.1, T1.4 (SEC_1), TP7.1, U1.1 (IN), U1.3 (EN)
~STIM_ON: Q1.2 (TR1_GATE), TP5.1

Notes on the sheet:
STIMULATION
I/O
3V3 Regulator
4V2 Regulator
POWER
Transformer

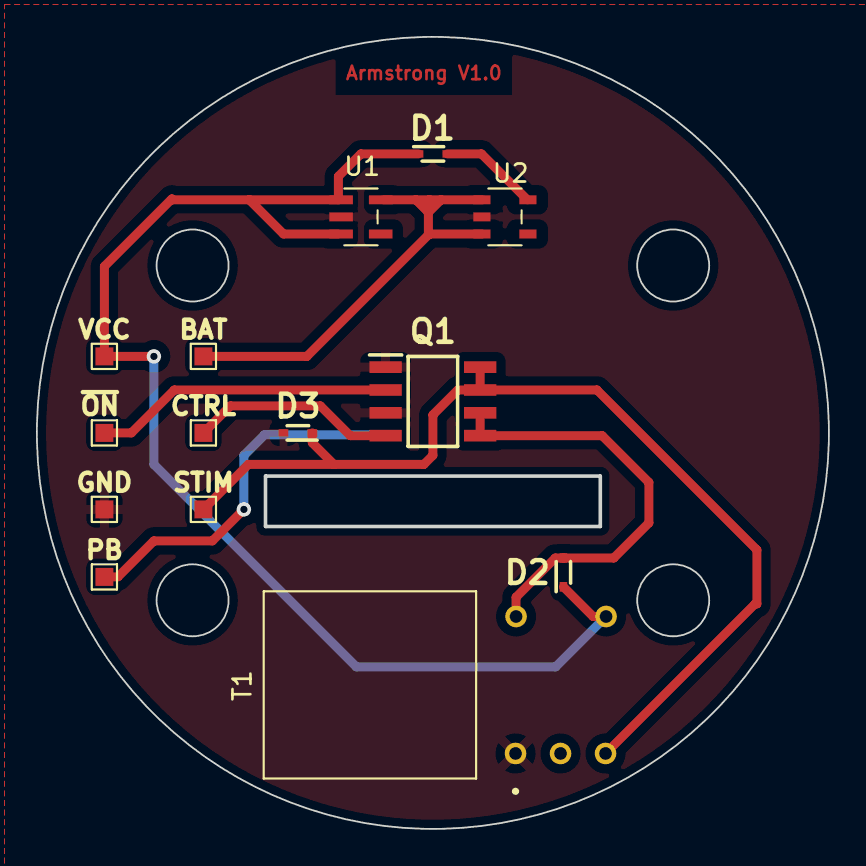
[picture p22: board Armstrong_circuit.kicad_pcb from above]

Board: 2 copper layers, 44.0 x 44.0 mm, 15 parts (1 on the bottom side), 9 nets.

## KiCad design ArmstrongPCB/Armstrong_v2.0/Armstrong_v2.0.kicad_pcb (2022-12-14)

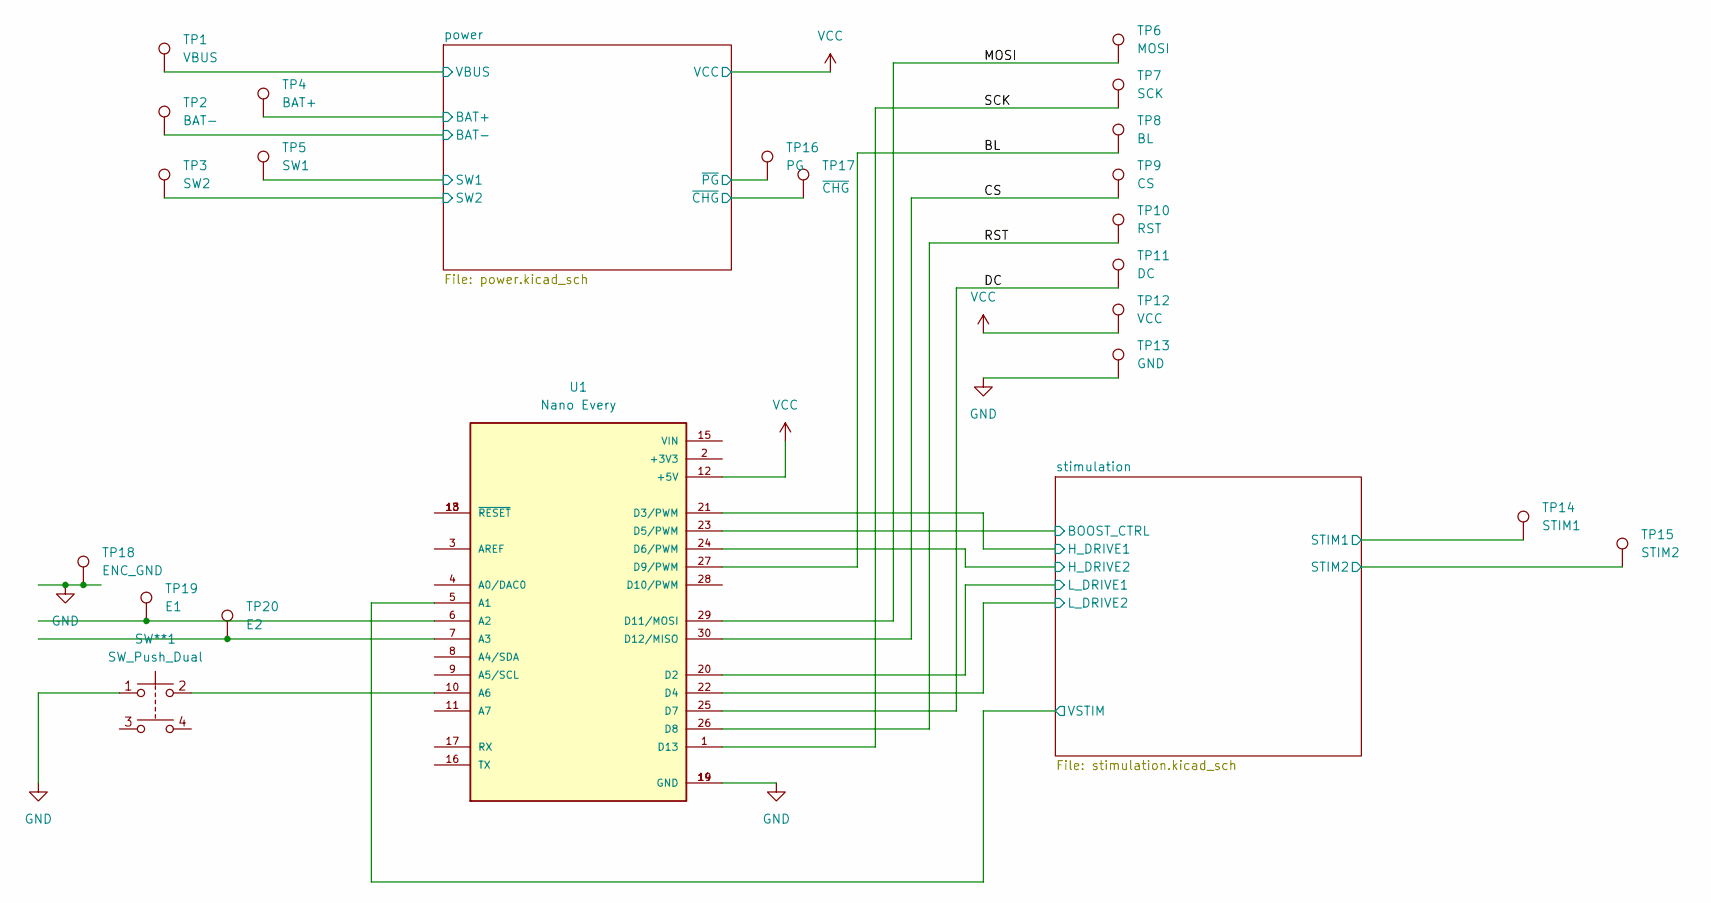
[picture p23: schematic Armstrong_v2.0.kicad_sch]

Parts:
SW**1: SW_Push_Dual; CS1204AF260-SMD
TP1: VBUS; TestPoint_THTPad_D2.0mm_Drill1.0mm
TP2: BAT-; TestPoint_THTPad_D2.0mm_Drill1.0mm
TP3: SW2; TestPoint_THTPad_D2.0mm_Drill1.0mm
TP4: BAT+; TestPoint_THTPad_D2.0mm_Drill1.0mm
TP5: SW1; TestPoint_THTPad_D2.0mm_Drill1.0mm
TP6: MOSI; TestPoint_Pad_D1.5mm
TP7: SCK; TestPoint_Pad_D1.5mm
TP8: BL; TestPoint_Pad_D1.5mm
TP9: CS; TestPoint_Pad_D1.5mm
TP10: RST; TestPoint_Pad_D1.5mm
TP11: DC; TestPoint_Pad_D1.5mm
TP12: VCC; TestPoint_Pad_D1.5mm
TP13: GND; TestPoint_Pad_D1.5mm
TP14: STIM1; TestPoint_THTPad_D2.0mm_Drill1.0mm
TP15: STIM2; TestPoint_THTPad_D2.0mm_Drill1.0mm
TP16: PG; TestPoint_Pad_D1.0mm
TP17: ~{CHG}; TestPoint_Pad_D1.0mm
TP18: ENC_GND; TestPoint_THTPad_D2.0mm_Drill1.0mm
TP19: E1; TestPoint_THTPad_D2.0mm_Drill1.0mm
TP20: E2; TestPoint_THTPad_D2.0mm_Drill1.0mm
U1: Nano Every; PARTREV 6-11-19

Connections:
/BL: TP8.1, U1.27 (D9/PWM)
/CS: TP9.1, U1.30 (D12/MISO)
/DC: TP11.1, U1.25 (D7)
/MOSI: TP6.1, U1.29 (D11/MOSI)
/RST: TP10.1, U1.26 (D8)
/SCK: TP7.1, U1.1 (D13)
/power/BAT+: TP4.1, TP5.1; also elsewhere on the board
/power/VBUS: TP1.1; also elsewhere on the board
/power/~CHG: TP17.1; also elsewhere on the board
/power/~PG: TP16.1; also elsewhere on the board
/stimulation/BOOST_CTRL: U1.23 (D5/PWM); also elsewhere on the board
/stimulation/H_DRIVE1: U1.21 (D3/PWM); also elsewhere on the board
/stimulation/H_DRIVE2: U1.24 (D6/PWM); also elsewhere on the board
/stimulation/L_DRIVE1: U1.20 (D2); also elsewhere on the board
/stimulation/L_DRIVE2: U1.22 (D4); also elsewhere on the board
/stimulation/STIM1: TP14.1; also elsewhere on the board
/stimulation/STIM2: TP15.1; also elsewhere on the board
/stimulation/VSTIM: U1.5 (A1); also elsewhere on the board
GND: SW**1.1, TP2.1, TP13.1, TP18.1, U1.14 (GND), U1.19 (GND); also elsewhere on the board
unnamed: TP19.1, U1.6 (A2)
unnamed: TP20.1, U1.7 (A3)
unnamed: SW**1.2, U1.10 (A6)
unnamed: U1.13 (~RESET), U1.18 (~RESET)
VCC: TP3.1, TP12.1, U1.12 (+5V); also elsewhere on the board

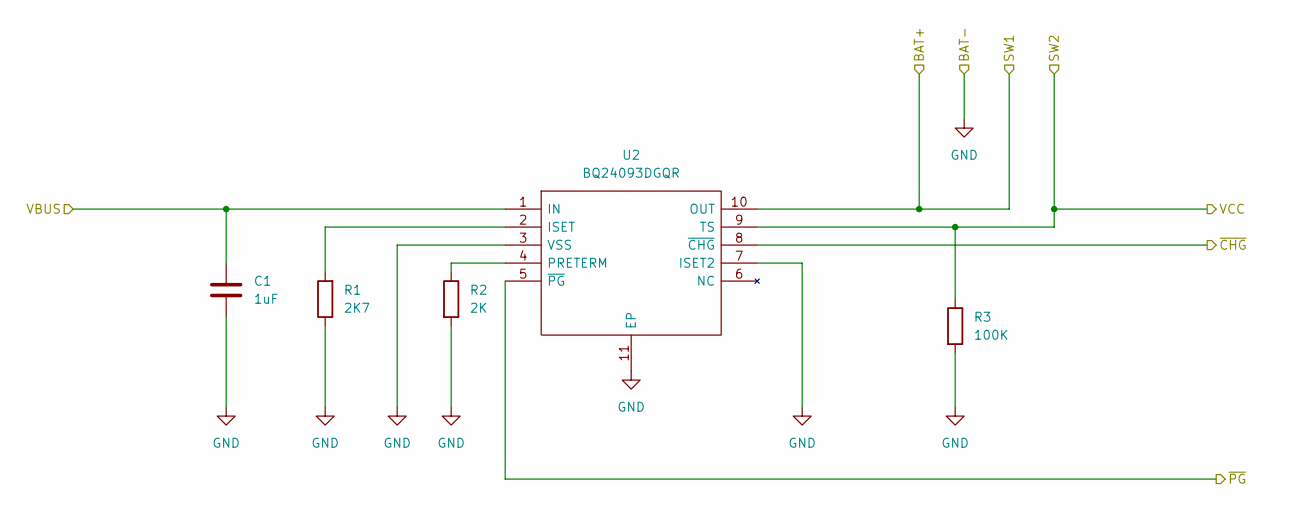
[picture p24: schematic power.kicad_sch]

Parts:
C1: 1uF; C_1206_3216Metric_Pad1.33x1.80mm_HandSolder
R1: 2K7; R_1206_3216Metric_Pad1.30x1.75mm_HandSolder
R2: 2K; R_1206_3216Metric_Pad1.30x1.75mm_HandSolder
R3: 100K; R_1206_3216Metric_Pad1.30x1.75mm_HandSolder
U2: BQ24093DGQR; Mouser Part Number 595-BQ24093DGQR

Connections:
/power/BAT+: U2.10 (OUT); also elsewhere on the board
/power/VBUS: C1.1, U2.1 (IN); also elsewhere on the board
/power/~CHG: U2.8 (~CHG); also elsewhere on the board
/power/~PG: U2.5 (~PG); also elsewhere on the board
GND: C1.2, R1.1, R2.2, R3.2, U2.3 (VSS), U2.7 (ISET2), U2.11 (EP); also elsewhere on the board
unnamed: R1.2, U2.2 (ISET)
unnamed: R2.1, U2.4 (PRETERM)
VCC: R3.1, U2.9 (TS); also elsewhere on the board

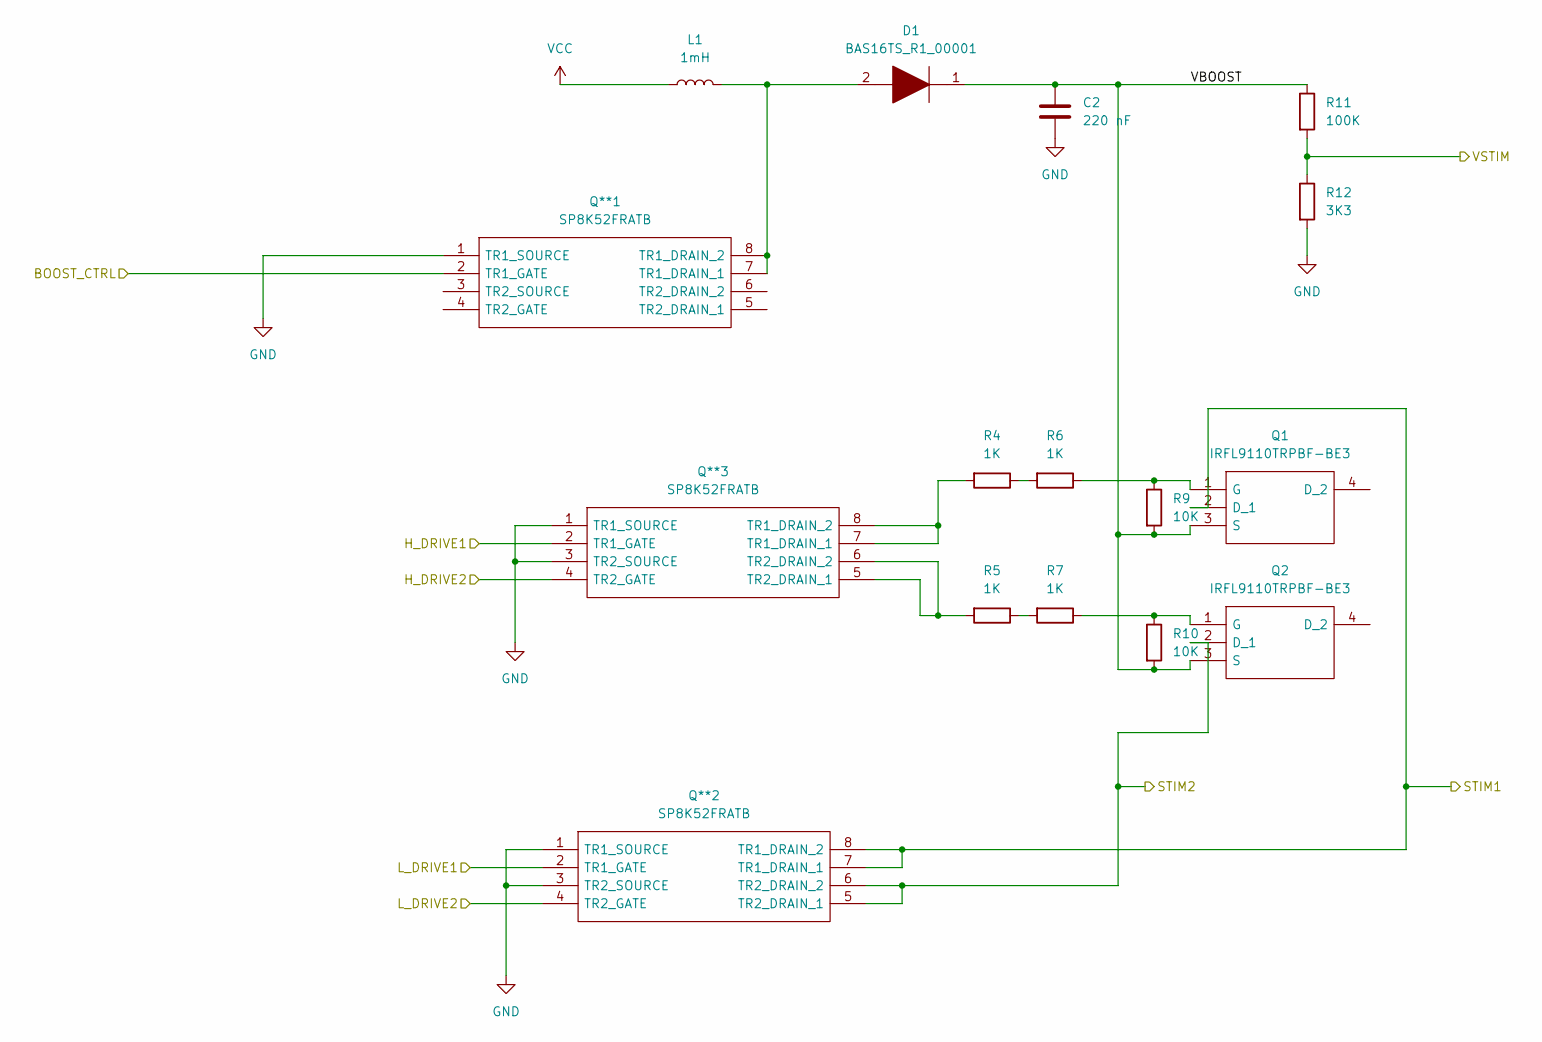
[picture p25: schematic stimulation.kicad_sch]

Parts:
C2: 220 nF; C_1206_3216Metric_Pad1.33x1.80mm_HandSolder
D1: BAS16TS_R1_00001; Manufacturer_Part_Number BAS16TS_R1_00001; Mouser Part Number 241-BAS16TS_R1_00001
L1: 1mH; LPS6225-105MRC
Q1, Q2: IRFL9110TRPBF-BE3; Mouser Part Number 78-IRFL9110TRPBF-BE3
Q**1, Q**2, Q**3: SP8K52FRATB; Manufacturer_Part_Number SP8K52FRATB; Mouser Part Number 755-SP8K52FRATB
R4, R5, R6, R7: 1K; R_1206_3216Metric_Pad1.30x1.75mm_HandSolder
R9, R10: 10K; R_1206_3216Metric_Pad1.30x1.75mm_HandSolder
R11: 100K; R_1206_3216Metric_Pad1.30x1.75mm_HandSolder
R12: 3K3; R_1206_3216Metric_Pad1.30x1.75mm_HandSolder

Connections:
/stimulation/BOOST_CTRL: Q**1.2 (TR1_GATE); also elsewhere on the board
/stimulation/H_DRIVE1: Q**3.2 (TR1_GATE); also elsewhere on the board
/stimulation/H_DRIVE2: Q**3.4 (TR2_GATE); also elsewhere on the board
/stimulation/L_DRIVE1: Q**2.2 (TR1_GATE); also elsewhere on the board
/stimulation/L_DRIVE2: Q**2.4 (TR2_GATE); also elsewhere on the board
/stimulation/STIM1: Q1.2 (D_1), Q**2.7 (TR1_DRAIN_1), Q**2.8 (TR1_DRAIN_2); also elsewhere on the board
/stimulation/STIM2: Q2.2 (D_1), Q**2.5 (TR2_DRAIN_1), Q**2.6 (TR2_DRAIN_2); also elsewhere on the board
/stimulation/VBOOST: C2.1, D1.1, Q1.3 (S), Q2.3 (S), R9.2, R10.2, R11.1
/stimulation/VSTIM: R11.2, R12.1; also elsewhere on the board
GND: C2.2, Q**1.1 (TR1_SOURCE), Q**2.1 (TR1_SOURCE), Q**2.3 (TR2_SOURCE), Q**3.1 (TR1_SOURCE), Q**3.3 (TR2_SOURCE), R12.2; also elsewhere on the board
unnamed: D1.2, L1.2, Q**1.7 (TR1_DRAIN_1), Q**1.8 (TR1_DRAIN_2)
unnamed: Q1.1 (G), R6.1, R9.1
unnamed: Q2.1 (G), R7.1, R10.1
unnamed: Q**3.5 (TR2_DRAIN_1), Q**3.6 (TR2_DRAIN_2), R5.2
unnamed: Q**3.7 (TR1_DRAIN_1), Q**3.8 (TR1_DRAIN_2), R4.2
unnamed: R4.1, R6.2
unnamed: R5.1, R7.2
VCC: L1.1; also elsewhere on the board

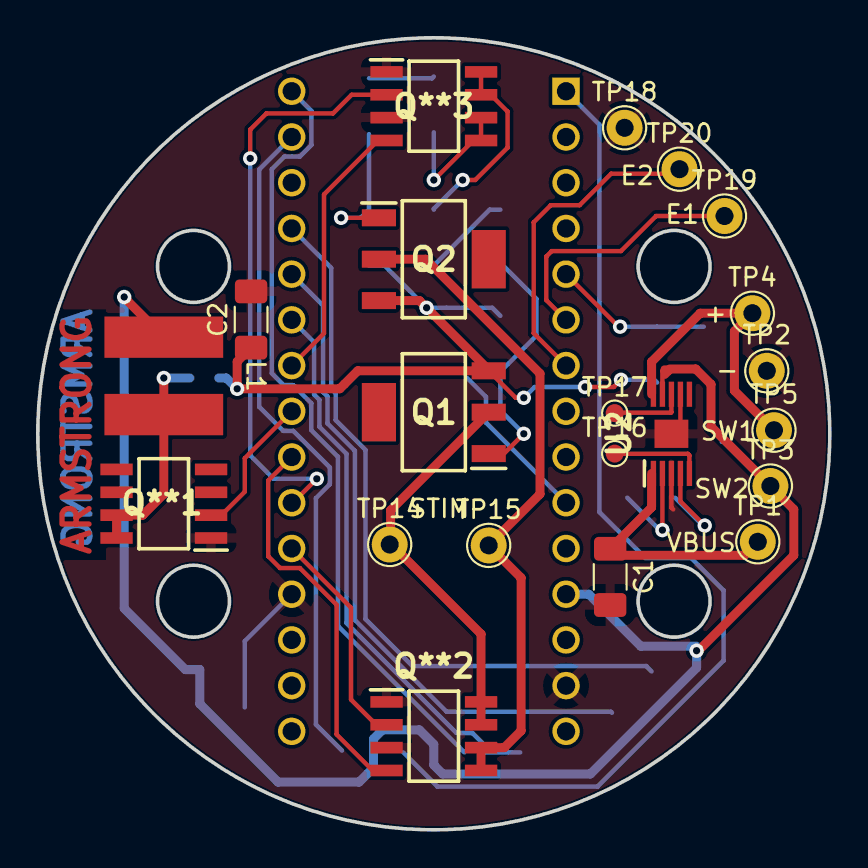
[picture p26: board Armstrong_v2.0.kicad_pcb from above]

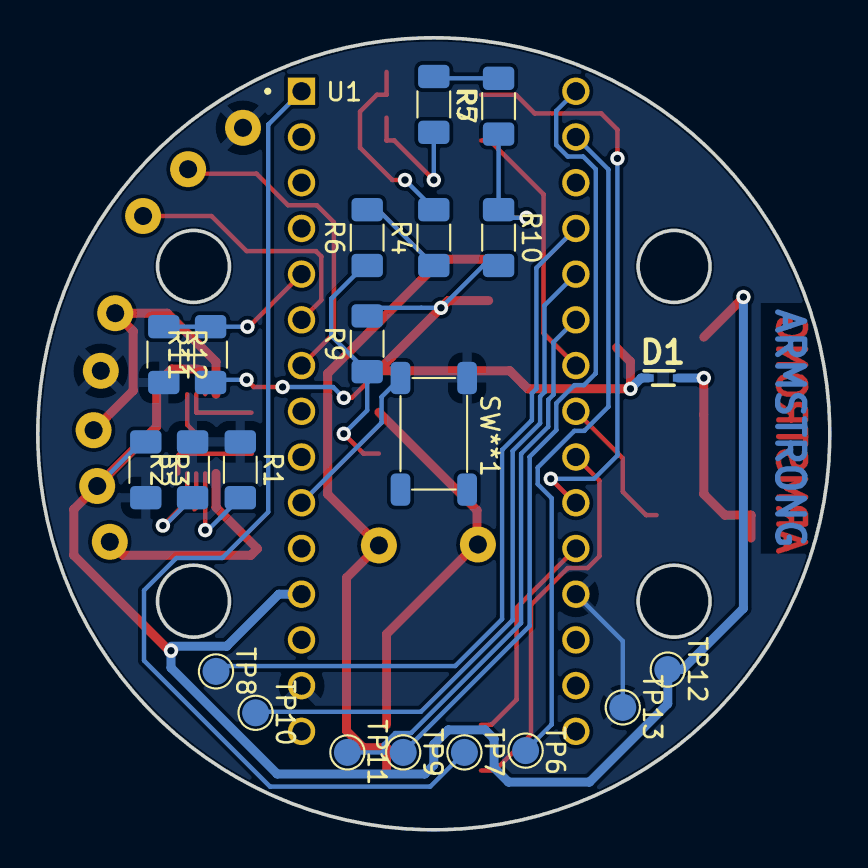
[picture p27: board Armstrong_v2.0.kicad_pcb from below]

Board: 2 copper layers, 44.0 x 44.0 mm, 43 parts (22 on the bottom side), 34 nets.

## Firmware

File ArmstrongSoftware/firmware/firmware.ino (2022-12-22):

#include "firmware.h"


const uint32_t boost_period_ticks = TCA_FREQ / BOOST_FREQ;
const uint8_t pulse_delay_ticks = 1;

volatile uint32_t ovf_count = 0;
volatile uint8_t dir = 0;

volatile uint32_t pulse_period_ovf;
volatile uint32_t pulse_duty_ovf;
volatile float boost_duty;
volatile uint8_t waveform_type;

void waveform_param_set(uint32_t frequency, float duty, float amplitude, enum waveform type) {
    if (type == OFF) {
        TCA0.SINGLE.CTRLA &= ~TCA_SINGLE_ENABLE_bm;
    } else {
        TCA0.SINGLE.CTRLA |= TCA_SINGLE_ENABLE_bm;
    }
    pulse_period_ovf = BOOST_FREQ / frequency;  // Amount of TCA0 overflows for pulse period
    pulse_duty_ovf = BOOST_FREQ / frequency * duty;  // Amount of TCA0 overflows for pulse duty
    boost_duty = amplitude;
    waveform_type = type;
}

unsigned long scaled_millis(void) {
    return millis() / 16;  // TCA is running 16 times the normal speed
}

void scaled_delay(unsigned long ms) {
    delay(ms * 16);  // TCA is running 16 times the normal speed
}

/* Turn on the high side to either output line
   direction:
        0 - line 1
        >= 1 - line 2
*/
static inline void set_pulse_line_on(uint8_t direction) {
    if (direction) {
        PORTF.OUTCLR = PIN5_bm;  // Turn off H_DRIVE1
        PORTC.OUTCLR = PIN6_bm;  // Turn off L_DRIVE2
        PORTA.OUTSET = PIN0_bm;  // Turn on L_DRIVE1
        PORTF.OUTSET = PIN4_bm;  // Turn on H_DRIVE2
    } else {
        PORTF.OUTCLR = PIN4_bm;  // Turn off H_DRIVE2
        PORTA.OUTCLR = PIN0_bm;  // Turn off L_DRIVE1
        PORTC.OUTSET = PIN6_bm;  // Turn on L_DRIVE2
        PORTF.OUTSET = PIN5_bm;  // Turn on H_DRIVE1
    }
}

static inline void set_pulse_line_off(void) {
    PORTF.OUTCLR = PIN5_bm;  // Turn off H_DRIVE1
    PORTF.OUTCLR = PIN4_bm;  // Turn off H_DRIVE2
}

void pulse_init(void) {
    // Digital writes
    PORTF.DIRSET = PIN5_bm;  // H_DRIVE1
    PORTF.DIRSET = PIN4_bm;  // H_DRIVE2
    PORTA.DIRSET = PIN0_bm;  // L_DRIVE1
    PORTC.DIRSET = PIN6_bm;  // L_DRIVE2

    // PWM TCA Output Channel
    PORTB.DIRSET = PIN2_bm;  // D5, PB2 TCA_CMP2

    // Timer A Setup
    #ifdef TCA_FREQ
    TCA0.SINGLE.CTRLA = TCA_SINGLE_CLKSEL_DIV4_gc;  // Set clock, TCA_FREQ should correspond to this div value
    #endif
    TCA0.SINGLE.CTRLB = TCA_SINGLE_CMP2EN_bm | TCA_SINGLE_WGMODE_SINGLESLOPE_gc;  // Single slope and enable channel 2
    TCA0.SINGLE.PERBUF = boost_period_ticks;  // Set the period
    TCA0.SINGLE.CMP2BUF = 0;  // Set the duty-cycle
    TCA0.SINGLE.INTCTRL = TCA_SINGLE_CMP2_bm | TCA_SINGLE_OVF_bm;  // Setup interrupts to fire on cmp2  

    // Initialize timing parameters
    waveform_param_set(100, 0, 0, OFF);

    // Enable timer
    TCA0.SINGLE.CTRLA |= TCA_SINGLE_ENABLE_bm;
}

ISR(TCA0_CMP2_vect) {
    TCA0.SINGLE.INTFLAGS |= TCA_SINGLE_CMP2_bm;
}

ISR(TCA0_OVF_vect) {
    if (ovf_count < pulse_duty_ovf + pulse_delay_ticks) {
        TCA0.SINGLE.CMP2BUF = boost_period_ticks * boost_duty;  // Set the duty-cycle
        if (ovf_count >= pulse_delay_ticks) {
            set_pulse_line_on(dir);
        }
    } else {
        set_pulse_line_off();
        // TCA0.SINGLE.CMP2BUF = 0;
    }

    if (ovf_count >= pulse_period_ovf - 1) {  // End of pulse period
        if (waveform_type == DIFFERENTIAL | waveform_type == ASCENDING_DIFFERENTIAL) {
            dir = ~dir;
        }
        ovf_count = 0;
    } else {
        ovf_count++;
    }

    TCA0.SINGLE.INTFLAGS |= TCA_SINGLE_OVF_bm;  // Clear interrupt flag
}

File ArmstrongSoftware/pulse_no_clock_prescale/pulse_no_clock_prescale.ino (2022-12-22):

#include <SPI.h>
#include "LCD_Driver.h"
#include "GUI_Paint.h"
// #include "image.h"

// Frequency data
int freq_vals[] = {2500, 1666, 1250, 1000, 833};
// int duty_cycle_vals[] = {50, 33, 25, 20, 17};
float duty_cycle_vals[] = {0.05, 0.04, 0.03, 0.02, 0.01}; // for 200Hz (1250): 50, 33, 25, 20, 17 ticks respectively

int freq_sel = 2;
int dCycle_sel = 3;

// Rotary Encoder Setup
#define CW 0    // Clockwise
#define CCW 1   // Counterclockwise

int a_in = 16;   // Rotary encoder switch at pin 2
int b_in = 17;   // Rotary encoder phase-shifted switch at pin 4
int curr_state;
int last_state;

int attribute_sel = 0;
int counter = 2;
String dir;

// Push button Setup
int pb_master = 20;

// LCD Communication Setup
char freq_buff[8];
char dCycle_buff[8];

// Clock setup
unsigned int minute = 0;
unsigned int hour = 0;
char min_buff[2];   // buffer
char hrs_buff[2];

// UI/UX menu attributes
enum
{
  freq,
  dutyCycle,
  none
} selected_attribute;

// Fucntion Prototypes
void lock_screen();
void unlocked_screen();
void update_freq(int freq);
void update_dCycle(int dCycle);
void select_freq();
void select_dutyCycle();
void update_clock(int min_p, int hrs_p);
void freq_up();
void freq_down();
void duty_cycle_up();
void duty_cycle_down();

void setup() 
{
  // System clock is 16 MHz
  // CLK_TCA is 250 KHz with a prescaler from system clock of 64
  // The longest period of TCA is (1/250 KHz) * 2^16 bits = 262 ms (lowest frequency of 4 Hz)
  // The resolution of TCA is 1/250 KHz = 4 us
  // The period of the 200 Hz PWM signal is (1/200 Hz) / 4 us = 1250 ticks
  // The pulse width of the 100 us pulse is 100 us / 4 us = 25 ticks
  pinMode(5, OUTPUT);
  analogWrite(5, 128);
  TCA0.SINGLE.CTRLA &= ~TCA_SINGLE_ENABLE_bm;  // Turn off timer while we change parameters.
  TCA0.SINGLE.PERBUF = freq_vals[freq_sel];         // select default frequency with 200 Hz
  int dCycle_tick = freq_vals[freq_sel] * duty_cycle_vals[dCycle_sel];  // Calculate duty cycle ticks
  TCA0.SINGLE.CMP2BUF = dCycle_tick;  // select default duty cycle as 0.02 (actual 0.98)
  TCA0.SINGLE.CTRLA |= TCA_SINGLE_ENABLE_bm;

  // ////////// External Interrupt Setup ///////////
  // attachInterrupt(digitalPinToInterrupt(2), freq_up, FALLING);  // use pin 2 for external interrupt trigger on falling edge
  // attachInterrupt(digitalPinToInterrupt(3), freq_down, FALLING);  // use pin 2 for external interrupt trigger on falling edge

  // Rotary switch input setup
  pinMode(a_in, INPUT_PULLUP);
  pinMode(b_in, INPUT_PULLUP);

  last_state = digitalRead(a_in);

  // Push button setup
  pinMode(pb_master, INPUT_PULLUP);

  // LCD Setup
  Config_Init();
  Serial.print("Initiating...\r\n");
  LCD_Init();
  LCD_SetBacklight(1000);
  Paint_NewImage(LCD_WIDTH, LCD_HEIGHT, 0, BLACK);

  // Display Lock Screen
  lock_screen();
  long myTime = -1;

  Serial.print("Break point 1\r\n");
  // Unlock mechanism: need to press down the button for at least 1 second to unlock
  int lock_counter = 0;
  update_clock(minute, hour);
  while (1) 
  {
    myTime++;
    Serial.println(myTime);
    if (myTime != 0 && myTime % 3600 == 0)
    {
      hour++;
      minute = 0;
      Serial.print("Clock update-> ");
      Serial.print(hour);
      Serial.print(" : ");
      Serial.println(minute);
      update_clock(minute, hour);
    }
    else if (myTime != 0 && myTime % 60 == 0)
    {
      minute++;
      Serial.print("Clock update-> ");
      Serial.print(hour);
      Serial.print(" : ");
      Serial.println(minute);
      update_clock(minute, hour);
    }
    bool locker = (bool) digitalRead(pb_master);
    if (!locker) 
    {
      if (lock_counter == 0) 
      {
        lock_counter++;
      } 
      else if (lock_counter == 1) 
      {
        lock_counter = 0;
        break;
      }
    } 
    else 
    {
      lock_counter = 0;
    }
    delay(999);
  }

  unlocked_screen();
  delay(2);
  Paint_Clear(BLACK);
  selected_attribute = none;
  display_stats(freq_vals[freq_sel], duty_cycle_vals[dCycle_sel]);
}

void loop() 
{ 
  // Menu level 1
  curr_state = digitalRead(a_in);
  if (curr_state != last_state && curr_state == 0) 
  {
    // Clockwise rotation once
    if(digitalRead(b_in) == curr_state) 
    {
      if (attribute_sel < 1) 
      {
        attribute_sel++;
        select_freq();
      }
      dir = "CCW";
    } 
    // Counter clockwise rotation once
    else 
    {
      if (attribute_sel > 0) 
      {
        attribute_sel--;
        select_dutyCycle();
      }
      dir = "CW";
    }
    Serial.print("Menu lvl 2: ");
    Serial.print("Direction: ");
    Serial.print(dir);
    Serial.print(" | attribute_sel: ");
    Serial.println(attribute_sel);
  }
  last_state = curr_state;
  delayMicroseconds(200);

  ///////////// Menu level 2 begins /////////////
  if (!digitalRead(pb_master))
  {
    // Menu lvl 1 -> selected to adjust freq
    if (selected_attribute == freq)
    {
      // Highlight confirmed attribute
      Serial.println("Freq is confirmed!");
      String freq_out = String(freq_vals[freq_sel]);
      freq_out.toCharArray(freq_buff, sizeof(freq_buff));
      Paint_DrawString_EN(12, 120, freq_buff, &Font16, BLACK, RED);   // Paint red to selected attribute text to highlight

      /////////// Menu lvl 2 while loop ///////////

      // Rotate to change selected attribute
      last_state = digitalRead(a_in);
      while(1)
      {
        curr_state = digitalRead(a_in);
        if (curr_state != last_state && curr_state == 0)
        {
          // Clockwise rotation once
          if(digitalRead(b_in) == curr_state) 
          {
            if (counter < 4) 
            {
              counter++;
              freq_up();
              // Serial.println("Freq up!");
              update_freq(freq_vals[freq_sel]);
            }
            dir = "CCW";
          } 
          // Counter clockwise rotation once
          else 
          {
            if (counter > 0) 
            {
              counter--;
              freq_down();
              // Serial.println("Freq down!");
              update_freq(freq_vals[freq_sel]);
            }
            dir = "CW";
          }
          Serial.print("Menu lvl 2: ");
          Serial.print("Direction: ");
          Serial.print(dir);
          Serial.print(" | Counter: ");
          Serial.print(counter);
          Serial.print(" | Freq_sel: ");
          Serial.println(freq_sel);
        }

        // return to the previous menu (lvl 1)
        if (!digitalRead(pb_master))
        {
          Serial.println("Exit menu lvl 2!");
          selected_attribute = none;
          String freq_out = String(freq_vals[freq_sel]);
          freq_out.toCharArray(freq_buff, sizeof(freq_buff));
          Paint_DrawString_EN(12, 120, freq_buff, &Font16, BLACK, WHITE);   // reset selected attribute color -> freq
          Paint_DrawString_EN(10, 70, "Freq", &Font16, BLACK, BLUE);
          break;
        }

        last_state = curr_state;
        delayMicroseconds(200);
      }
      /////////// End menu lvl 2 while loop ///////////

    }
    // Menu lvl 1 -> selected to adjust duty cycle
    else if (selected_attribute == dutyCycle)
    {
      // Highlght confirmed attribute
      Serial.println("Duty cycle is confirmed!");
      String dCycle_out = String(duty_cycle_vals[dCycle_sel]);
      dCycle_out.toCharArray(dCycle_buff, sizeof(dCycle_buff));
      Paint_DrawString_EN(110, 120, dCycle_buff, &Font16, BLACK, RED);    // Paint red to selected attribute text to highlight

      /////////// Menu lvl 2 while loop ///////////

      // Rotate to change selected attribute
      last_state = digitalRead(a_in);
      while(1)
      {
        curr_state = digitalRead(a_in);
        if (curr_state != last_state && curr_state == 0) 
        {
          // Clockwise rotation once
          if(digitalRead(b_in) == curr_state) 
          {
            if (counter < 4) 
            {
              counter++;
              duty_cycle_up();
              update_dCycle(duty_cycle_vals[dCycle_sel]);
            }
            dir = "CCW";
          } 
          // Counter clockwise rotation once
          else 
          {
            if (counter > 0) 
            {
              counter--;
              duty_cycle_down();
              update_dCycle(duty_cycle_vals[dCycle_sel]);
            }
            dir = "CW";
          }
          Serial.print("Menu lvl 2: ");
          Serial.print("Direction: ");
          Serial.print(dir);
          Serial.print(" | Counter: ");
          Serial.print(counter);
          Serial.print(" | duty cycle select: ");
          Serial.println(dCycle_sel);
        }

        // return to the previous menu (lvl 1)
        if (!digitalRead(pb_master))
        {
          Serial.println("Exit menu lvl 2!");
          selected_attribute = none;
          String dCycle_out = String(duty_cycle_vals[dCycle_sel]);
          dCycle_out.toCharArray(dCycle_buff, sizeof(dCycle_buff));
          Paint_DrawString_EN(110, 120, dCycle_buff, &Font16, BLACK, WHITE);
          Paint_DrawString_EN(10, 70, "Freq", &Font16, BLACK, BLUE);
          break;
        }

        last_state = curr_state;
        delayMicroseconds(200);
      }
      /////////// End menu lvl 2 while loop ///////////

    } 
    // Menu lvl 1 -> nothing is selected
    else
    {
      // display current frequency value
      String freq_out = String(freq_vals[freq_sel]);
      freq_out.toCharArray(freq_buff, sizeof(freq_buff));
      Paint_DrawString_EN(12, 120, freq_buff, &Font16, BLACK, WHITE);

      // display current duty cycle value
      String dCycle_out = String(duty_cycle_vals[dCycle_sel]);
      dCycle_out.toCharArray(dCycle_buff, sizeof(dCycle_buff));
      Paint_DrawString_EN(110, 120, dCycle_buff, &Font16, BLACK, WHITE);
    }

    // switch(selected_attribute)
    // {
    //   case dutyCycle:
    //     Serial.println("Duty cycle is confirmed!");
    //     String dCycle_out = String(50);
    //     dCycle_out.toCharArray(dCycle_buff, sizeof(dCycle_buff));
    //     Paint_DrawString_EN(110, 120, dCycle_buff, &Font16, BLACK, RED);
    //     break;

    //   case freq:
    //     Serial.println("Freq is confirmed!");
    //     String freq_out = String(freq_vals[freq_sel]);
    //     freq_out.toCharArray(freq_buff, sizeof(freq_buff));
    //     Paint_DrawString_EN(12, 120, freq_buff, &Font16, BLACK, RED);
    //     break;
    // }
  }
  
  // delay(1);
}

// LCD functions
void lock_screen()
{
  Paint_Clear(BLACK);
  Paint_DrawString_EN(10, 123, "Press to Unlock", &Font20, BLACK, GREEN);
}

void unlocked_screen()
{
  Paint_Clear(BLACK);
  Paint_DrawString_EN(10, 123, "Unlocked", &Font20, BLACK, BLUE);
}

void display_stats(int freq, float dCycle)
{
  String freq_out = String(freq);
  String dCycle_out = String(dCycle);
  freq_out.toCharArray(freq_buff, sizeof(freq_buff));
  dCycle_out.toCharArray(dCycle_buff, sizeof(dCycle_buff));
  Paint_DrawString_EN(10, 70, "Freq", &Font16, BLACK, BLUE);
  Paint_DrawString_EN(12, 120, freq_buff, &Font16, BLACK, WHITE);
  Paint_DrawString_EN(80, 70, "Duty Cycle (%)", &Font16, BLACK, BLUE);
  Paint_DrawString_EN(110, 120, dCycle_buff, &Font16, BLACK, WHITE);
}

void update_freq(int freq)
{
  String freq_out = String(freq);
  freq_out.toCharArray(freq_buff, sizeof(freq_buff));
  Paint_DrawString_EN(12, 120, freq_buff, &Font16, BLACK, RED);
}
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

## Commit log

2022-11-25 Init master senior design repo
    [Base.stl, Bezel.stl, Screen.stl, Shaft.stl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]
2022-12-14 add deliverables folder
    [ADP122AUJZ-3-3-R7.stp, ADP162AUJZ-4.2-R7.stp, Armstrong_circuit.kicad_pcb, Armstrong_circuit.kicad_sch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]
2022-12-14 Add mechanical to deliverables
    [Base.stl, Bezel.stl, Enclosure v49.f3z, Screen.stl]
2022-12-14 Add BOM to delivarables
    [BOM.xlsx]
2022-12-22 Move submodules into this repo
    [ADP122AUJZ-3-3-R7.stp, ADP162AUJZ-4.2-R7.stp, Armstrong_circuit.kicad_pcb, Armstrong_circuit.kicad_sch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]

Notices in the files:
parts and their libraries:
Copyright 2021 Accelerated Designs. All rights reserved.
